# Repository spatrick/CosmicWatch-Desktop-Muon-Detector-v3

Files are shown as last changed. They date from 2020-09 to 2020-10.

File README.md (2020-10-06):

# CosmicWatch-Desktop-Muon-Detector

This repository if for the supplementary material used to build the CosmicWatch Desktop Muon Detectors V3

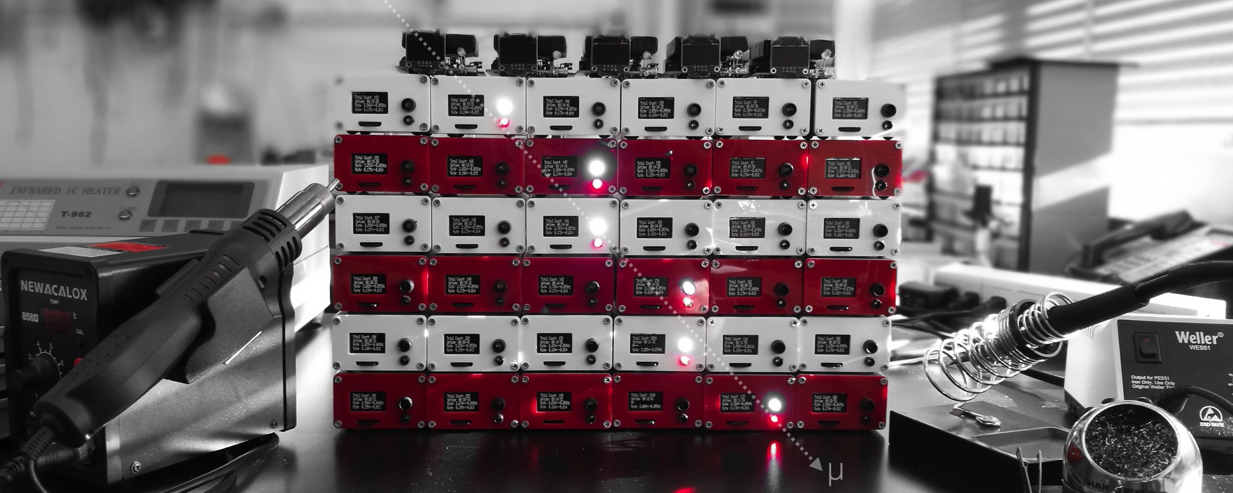
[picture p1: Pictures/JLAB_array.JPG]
screes


Currently, this version of the detector is only used for the MIT Junior Lab. 

Youtube videos describing various aspects of the detectors can be found here:

https://www.youtube.com/watch?v=Js-lOOS7sVE&list=PL4vQqHrEDYfFACdG83gTlRTslMXRjHihq

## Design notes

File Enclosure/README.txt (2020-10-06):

The enclosures were manufactured by enclosures and cases.
http://www.enclosuresandcasesinc.com/

The part number is 2506-2.56” with black and white silk screening on both sides.

The silkscreen, and dimensions are contained in this folder.

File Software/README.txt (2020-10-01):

This folder contains:

1. The Software.ino code. 
This file is the brains of the detector. You can upload it to the detector yourself, if you like, by installing the Arduino IDE, and then TeensyDuino. The code is well annotated, and if you don't plan on adding any extra features, I've added a couple of user options in the first few lines of the code.

2. The pitches.h file is simple the definition of various notes. That's right, you can have your detector play music.	You do not need to know how to use this file.

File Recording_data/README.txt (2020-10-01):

This folder contains:

1. The import_data.py code. 
This file can be run using python to communicate with your detector. The purpose of using this, rather than say the microSD card, is that the timestamp of each event would come from the computer rather than the Teensy, and is therefore more likely to be more accurate. You can also use this code to record multiple detectors to a single file. If you connect multiple detectors to your computer via a USB hub (or multiple USB ports), you can select multiple detectors to record data from using a ',' between names when prompted. This code requires several libraries, including Pyserial and Tornado -- these are available through pip.

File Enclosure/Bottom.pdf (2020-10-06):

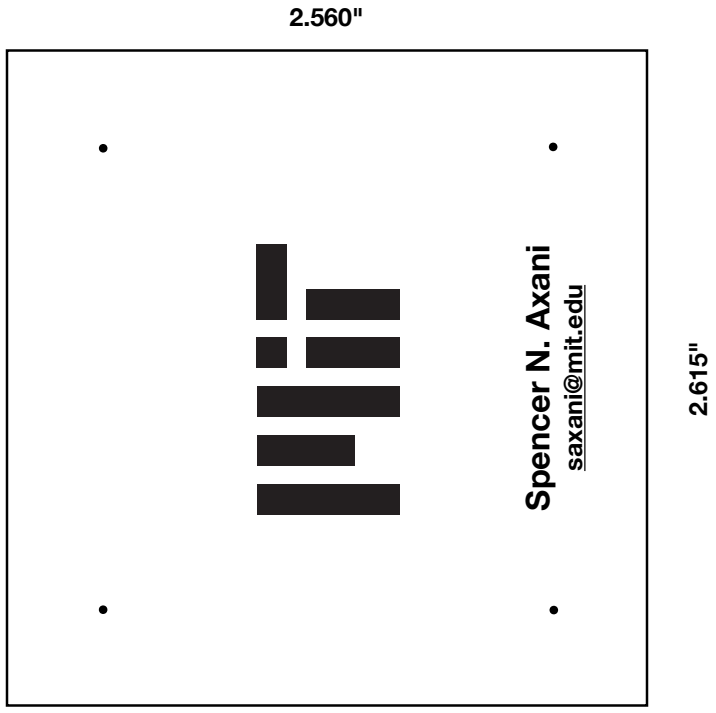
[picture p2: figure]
Spencer N. Axani; saxani@mit.edu

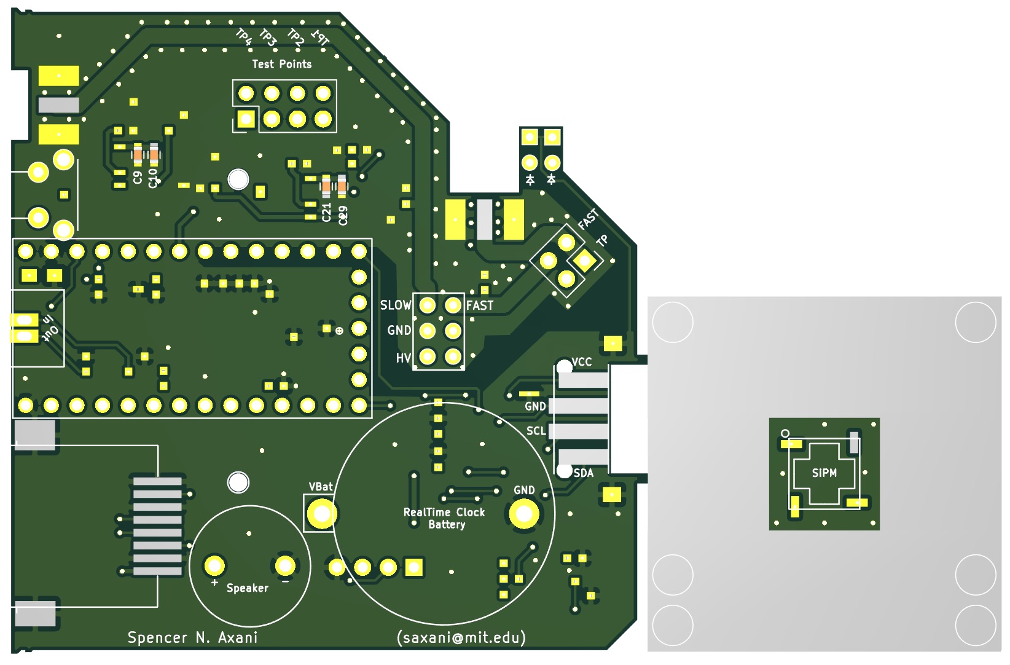
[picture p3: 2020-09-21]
Electronics/PCB_Top.JPG

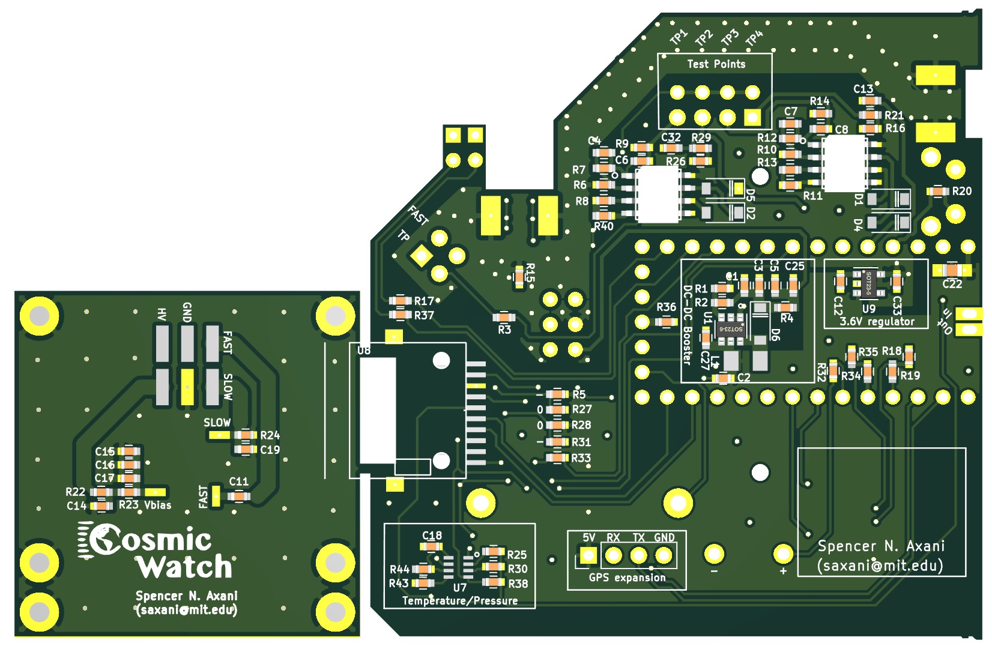
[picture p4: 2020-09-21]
Electronics/PCB_Bottom.JPG

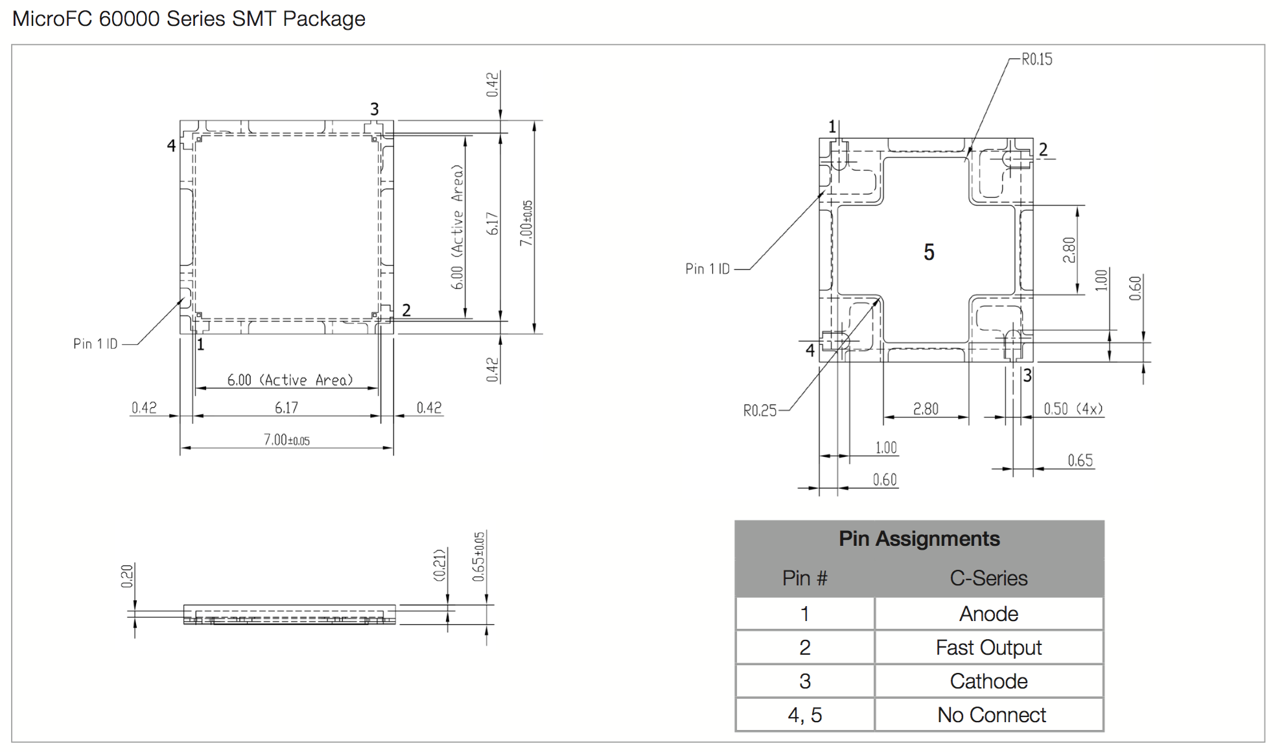
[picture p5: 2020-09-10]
Technical_drawings/SiPM.png

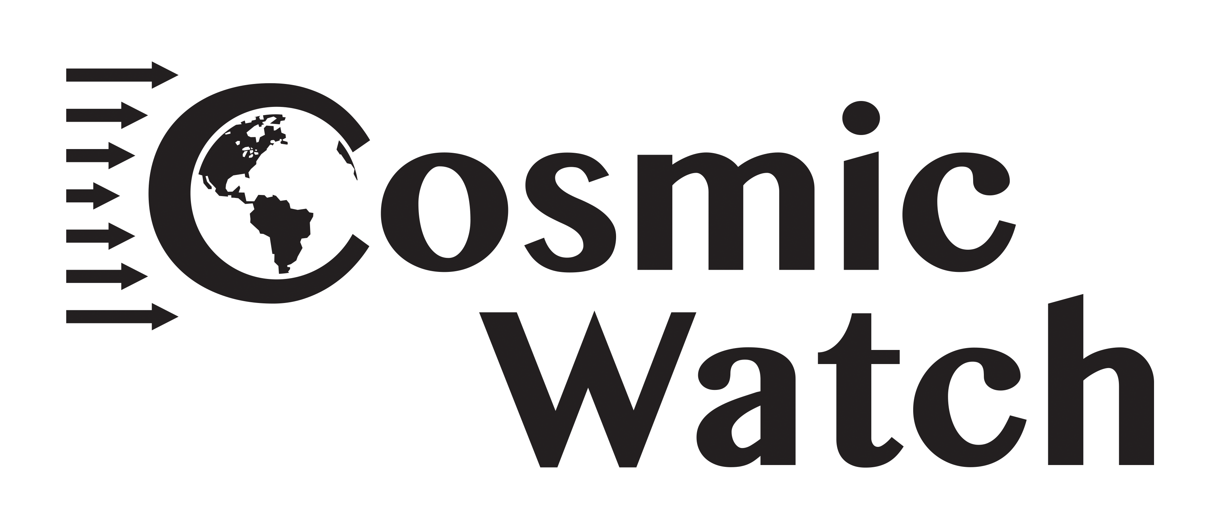
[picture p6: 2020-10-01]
Plotting/Example_data/CosmicWatch_Black.png

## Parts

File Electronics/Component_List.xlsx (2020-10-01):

Component List |  | Buy Extras
Item | Name | Number needed | Unit cost | Discription | Link
1 | SiPM | 1 | 66$ | MICROFC-60035-SMT-TR1 | https://www.digikey.com/product-detail/en/on-semiconductor/MICROFC-60035-SMT-TR1/MICROFC-60035-SMT-TR1OS-ND/9744774
2 | Reset button | 1 | 0.01 | SWITCH TACTILE SPST-NO 0.02A 15V | Digikey part number: P12215S-ND
3 | 3.6V regulator | 1 | 0.01 | TCR2EF36LM(CTCT-ND | https://www.digikey.com/product-detail/en/toshiba-semiconductor-and-storage/TCR2EF36-LM-CT/TCR2EF36LM-CTCT-ND/10380155
4 | DC-DC Booster | 1 | 0.01 | Boost Switching Regulator IC Positive Adjustable 3V 1 Output 260mA (Switch) SOT-23-6 | Digikey part number: MAX5026EUT+TCT-ND
5 | Op Amp LT1807 | 2 | 0.01 | General Purpose Amplifier 2 Circuit Rail-to-Rail 8-SO | Digikey part number: LT1807CS8#PBF-ND
6 | BMP280 temp/pressure | 1 | 0.01 | Pressure Sensor 4.35PSI ~ 15.95PSI (30kPa ~ 110kPa) Absolute 16b 8-SMD | Digikey part number: 828-1064-1-ND
7 | 6-pin connector | 1 | 0.01 | 6-pin connector for SiPM PCB | Digikey Part Number: WM17457-ND
8 | 6-pin header | 1 | 0.01 | 6-pin header for Main PCB | Digikey Part Number: 1212-1229-ND
9 | Jumper | 2 | 0.01 | CONN JUMPER SHORTING .100" GOLD | Digikey Part number: S9337-ND
10 | RJ45 Connector | 1 | 0.01 | CONN MOD JACK 8P8C R/A SHLD | Digikey Part Number: RJLSE4118101-ND
11 | 2.32k resistors | 1 | 0.01 | RMCF0603FT2K32CT-ND | https://www.digikey.com/product-detail/en/stackpole-electronics-inc/RMCF0603FT2K32/RMCF0603FT2K32CT-ND/2418013
12 | 13pF capacaitor | 2 | 0.01 | 1292-1483-1-ND | https://www.digikey.com/product-detail/en/walsin-technology-corporation/0603N130J500CT/1292-1483-1-ND/9355487
13 | 147k resistor | 1 | 0.01 | RES 147K OHM 1% 1/10W 0603 | RMCF0603FT147K‎
14 | 6.65k | 1 | 0.01 | RES 6.65K OHM 1% 1/10W 0603 | RMCF0603FT6K65‎
15 | 0Ohm resistor | 1 | 0.01 | RES 0 OHM JUMPER 1/10W 0603 | RMCF0603ZT0R00‎
16 | 49.9 resistor | 1 | 0.01 | RES 49.9 OHM 1% 1/10W 0603 | RMCF0603FT49R9‎
17 | 10nF capacitor | 1 | 0.01 | CAP CER 10000PF 50V X7R 0603 | 0603B103K500CT‎
18 | 1uF capacitor | 1 | 0.01 | CAP CER 1UF 50V X5R 0603 | ‎CL10A105KB8NNNC‎
19 | 100 resistor | 1 | 0.01 | RES 100 OHM 1% 1/10W 0603 | RMCF0603FT100R‎
20 | 1k resistor | 1 | 0.01 | RES 1K OHM 1% 1/10W 0603 | RMCF0603FT1K00‎
21 | 150 | 2 | 0.01 | RES 150 OHM 1% 1/10W 0603 | RMCF0603FT150R‎
22 | 10k | 1 | 0.01 | RES 10K OHM 1% 1/10W 0603 | RMCF0603FT10K0‎
23 | 6.8uF tantalum cap | 1 | 0.01 | CAP TANT 6.8UF 10% 16V 1206 | 478-1670-1-ND (https://www.digikey.com/product-detail/en/avx-corporation/TAJA685K016RNJ/478-1670-1-ND/564702)
24 | 47uH inductor | 1 | 0.01 | FIXED IND 47UH 170MA 1.3 OHM SMD | Digikey Part Number: 490-4063-1-ND
25 | Schottky diode | 2 | 0.01 | DIODE SCHOTTKY 40V 500MA SOD123 | Digikey Part Number: MBR0540CT-ND
26
27 | Standoff for SiPM PCB | 2 | 0.42 | 1/8" Hex Size, 7/16"" Length, 0-80 Thread Size | McMasterCarr part number: 91780A029
28 | Standoff threaded screws 0-80 | 4 | 1.00 | 0-80 Thread Size, 1/4" Long | McMasterCarr part number: 91771A055
29 | Plastic scintillator screws | 4 | 1.00 | 18-8 Stainless Steel, Number 0 Size, 5/16" Long | McMasterCarr part number: 92470A024
30
31 | microSD cards | 1 | 3$ | 6 packs of 10, 16GB | https://www.amazon.com/gp/product/B07RPVH4QQ/ref=ppx_yo_dt_b_asin_title_o03_s00?ie=UTF8&th=1
32 | 5mm Red LED | 1 | 0.01 | 1 pack of 100
33 | 3mm Red LED | 1 | 0.01 | 1 pack of 100 | https://www.amazon.com/Transparent-Lighting-Electronics-Components-Emitting/dp/B01AUI4VX8
34 | Micro USB cables | 1 | 0.01 | 10inch usb cable | https://www.amazon.com/DETHINTON-Braided-Charging-Samsung-Motorola/dp/B077S58W99
35 | OLED screen | 1 | 0.01 | 10 x 6pcs OLED screens. Need 60 screens. | https://www.amazon.com/Dorhea-Display-SSD1306-Self-Luminous-Raspberry/dp/B07WPCPM5H
36 | SMA connectors | 2 | 0.01 | side mount, with nut , we need a totla of 120 of them. | ` (https://www.amazon.com/Yootop-Female-Connectors-Center-Connector/dp/B07CMNDD3J?cv_ct_cx=sma+connectors)
37 | Test point headers | 1 | 0.01 | 90 degree header. Need 1x 10pcs 40pin | https://www.amazon.com/gp/product/B07XT8DYMW/ref=ox_sc_saved_title_1?smid=A10PG8DP5LW0Q1&psc=1
38 | Buzzer | 1 | 0.01 | Sound buzzer | https://www.amazon.com/Gikfun-Terminals-Passive-Electronic-Arduino/dp/B01GJLE5BS
39 | Battery case | 1 | 0.01 | 50 total batteries is fine | https://www.amazon.com/gp/product/B01JYNDZF0/ref=ppx_yo_dt_b_asin_title_o03_s00?ie=UTF8&psc=1
40 | Battery | 1 | 0.01 | 50 total batteries is fine | https://www.amazon.com/gp/product/B078GC5K81/ref=ppx_yo_dt_b_asin_title_o03_s00?ie=UTF8&psc=1
41 | RJ45 cable | 1 | 0.01 | we need 60 RJ45 cables, 6inch is what I'm suggesting | https://www.amazon.com/gp/product/B07ZNWSVLV/ref=ppx_yo_dt_b_asin_title_o06_s01?ie=UTF8&psc=1
42 | Header pins for Teensy | 1 | 0.01 | 1 pack of headers is fine | https://www.amazon.com/Breakaway-Header-Straight-Connector-Prototype/dp/B07BXDYTBP
43 | Electrical tape | 1 | 0.01 | 6pack of tape should work | https://www.amazon.com/Cambridge-Electrical-Black-Professional-Listed/dp/B0143LD8QY
44 | Aluminum foil | 1 | 0.10 | 100cm^2 aluminum foil | https://www.amazon.com/Amazon-Brand-Solimo-Aluminum-Square/dp/B07WDNGB82
45
46 | PCB | 1 | 1.00 | Printed circuit board | https://www.elecrow.com/pcb-manufacturing.html
47 | Acrylic faceplates | 1 | 1.00 | Front and back face plates | https://www.elecrow.com/acrylic-cutting.html
48 | Aluminum case | 1 | 5.00 | 2506-2.56" Clear Anodize case with 8 screws | http://www.enclosuresandcasesinc.com/
49
50 | Teensy4.0 | 1 | 20$ |  | https://www.pjrc.com/store/teensy40.html

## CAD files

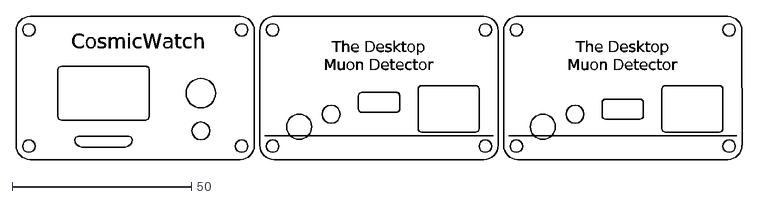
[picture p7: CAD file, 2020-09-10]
Technical_drawings/Faceplates.dxf
CosmicWatch
The Desktop Muon Detector

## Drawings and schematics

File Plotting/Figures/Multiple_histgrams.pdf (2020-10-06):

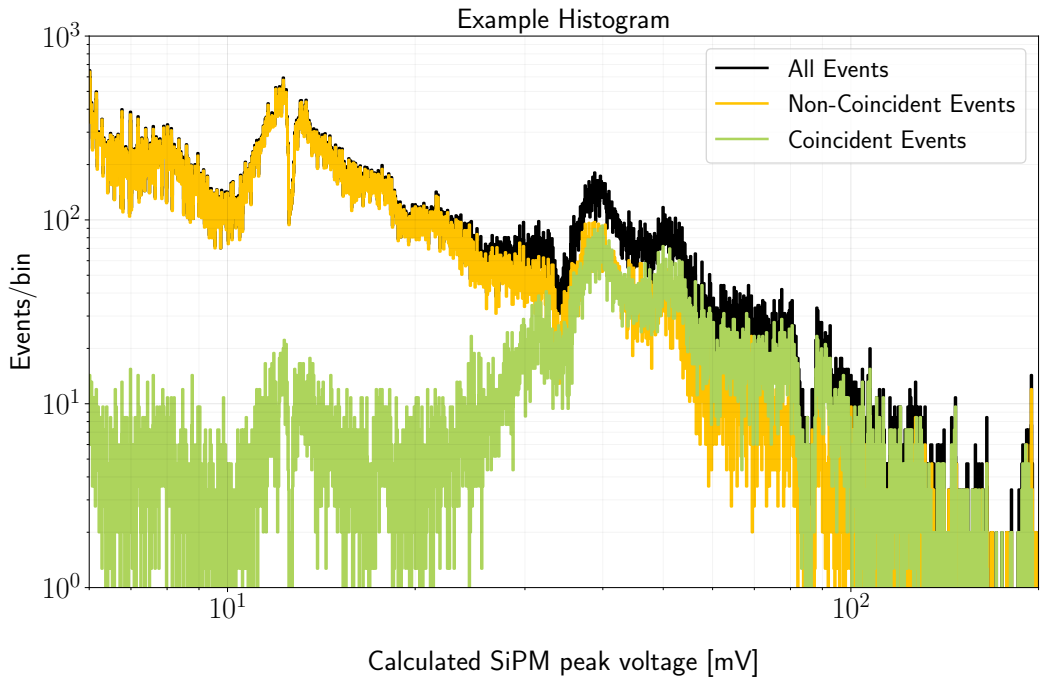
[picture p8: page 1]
Events/bin; Example Histogram; All; Events

Non-Coincident Events
Coincident Events

Calculated SiPM peak voltage [mV]

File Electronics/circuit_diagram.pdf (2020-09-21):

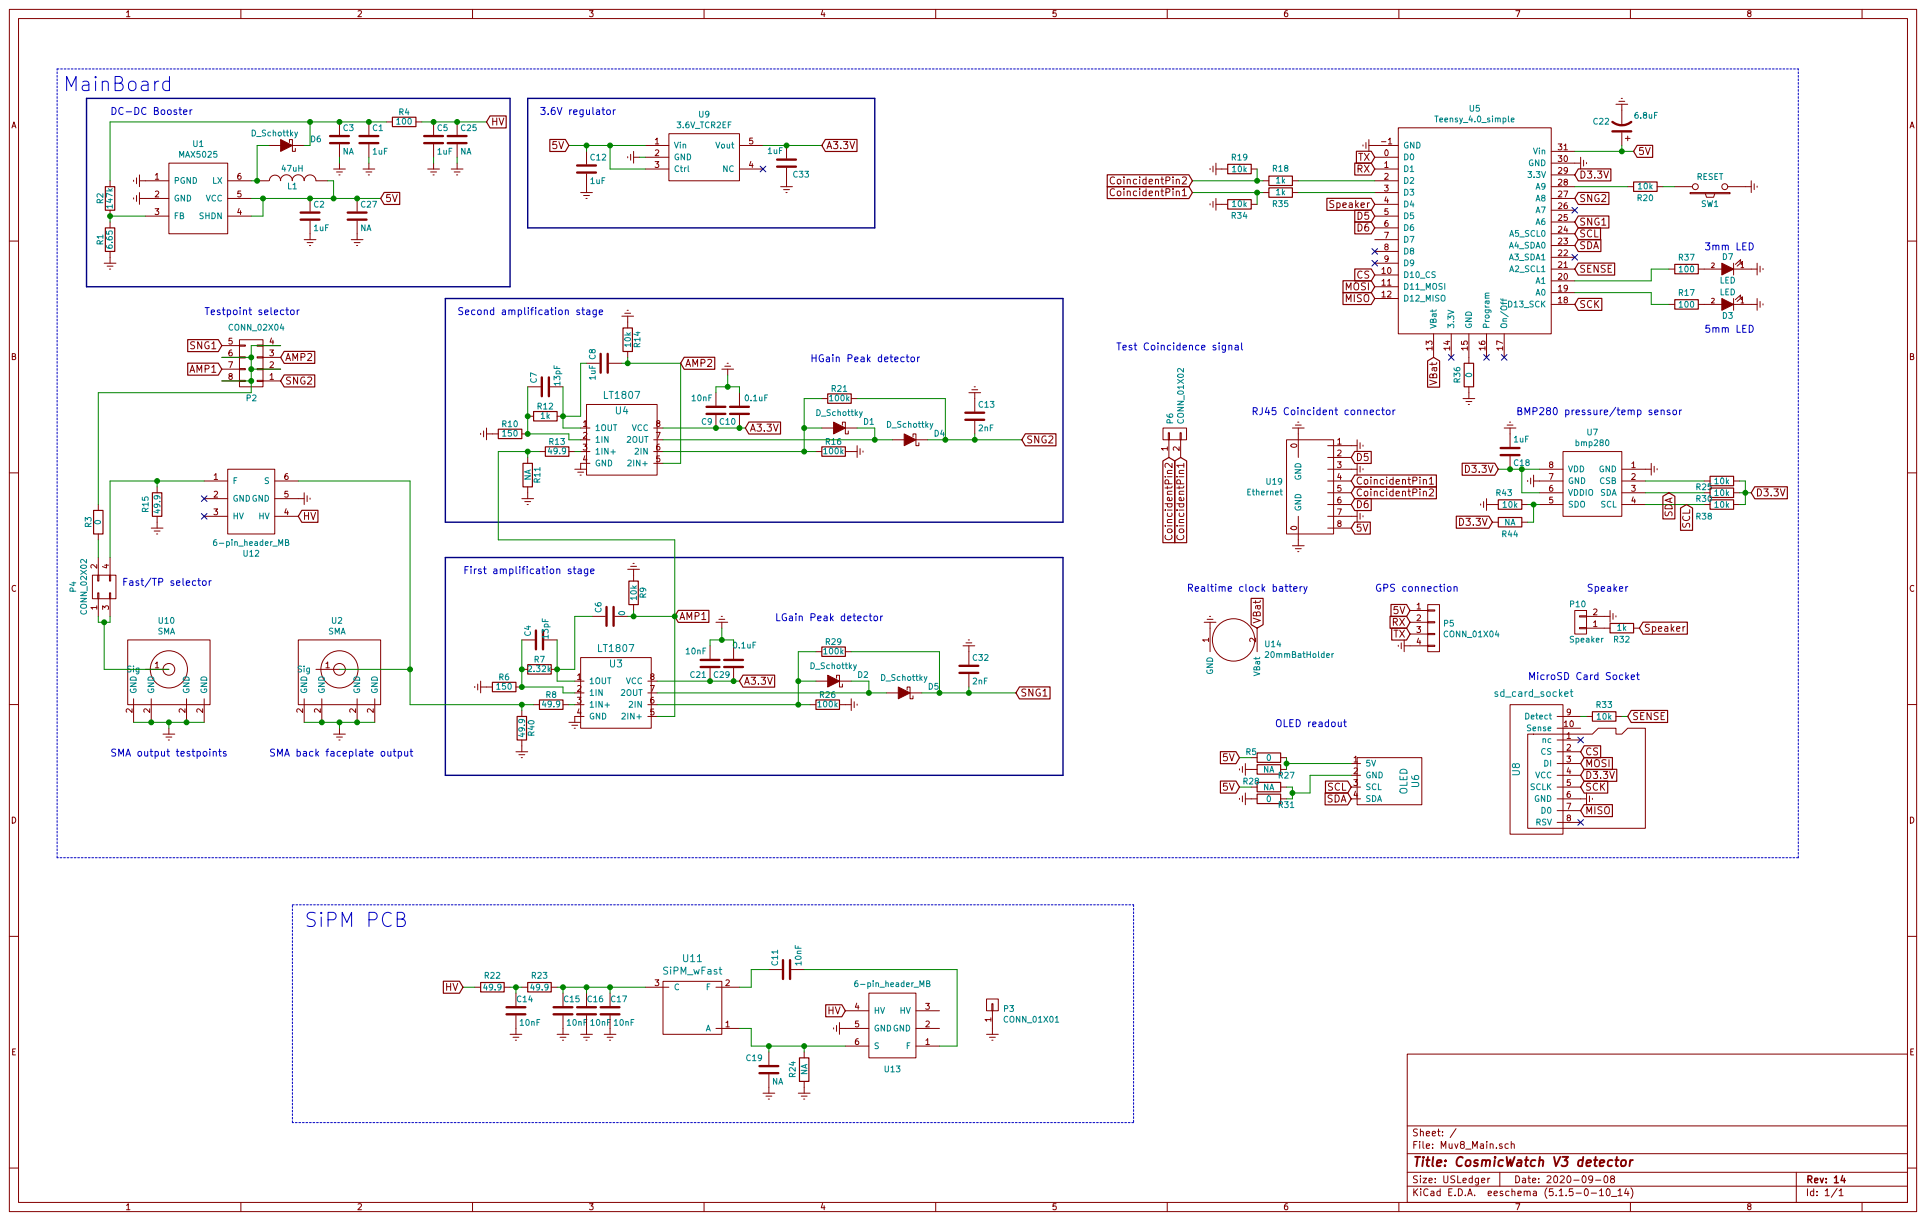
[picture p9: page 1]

Id: 1/1 Title: CosmicWatch V3 detector

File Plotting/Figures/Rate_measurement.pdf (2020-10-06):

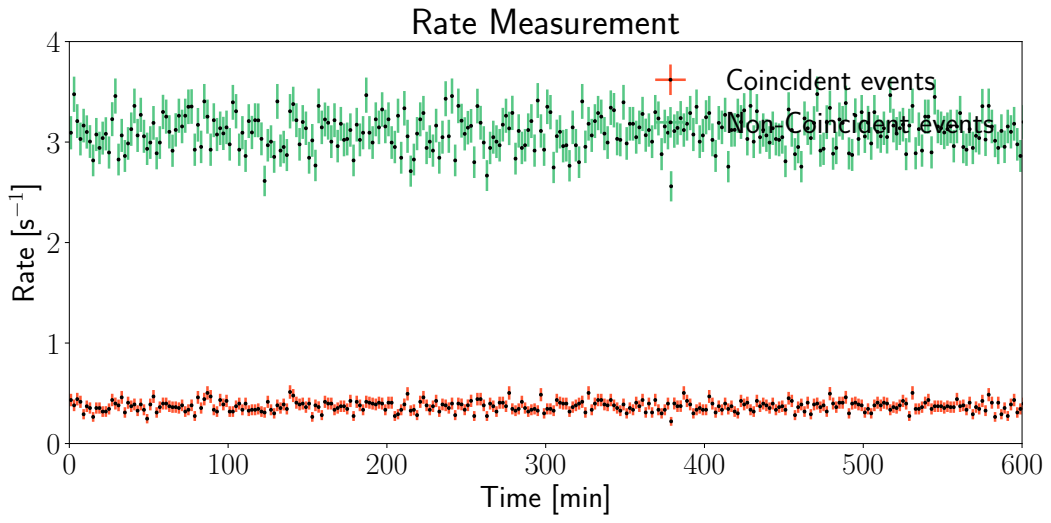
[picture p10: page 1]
Time [min]; Rate [s; Rate Measurement; Coincident events; Non-Coincident; events

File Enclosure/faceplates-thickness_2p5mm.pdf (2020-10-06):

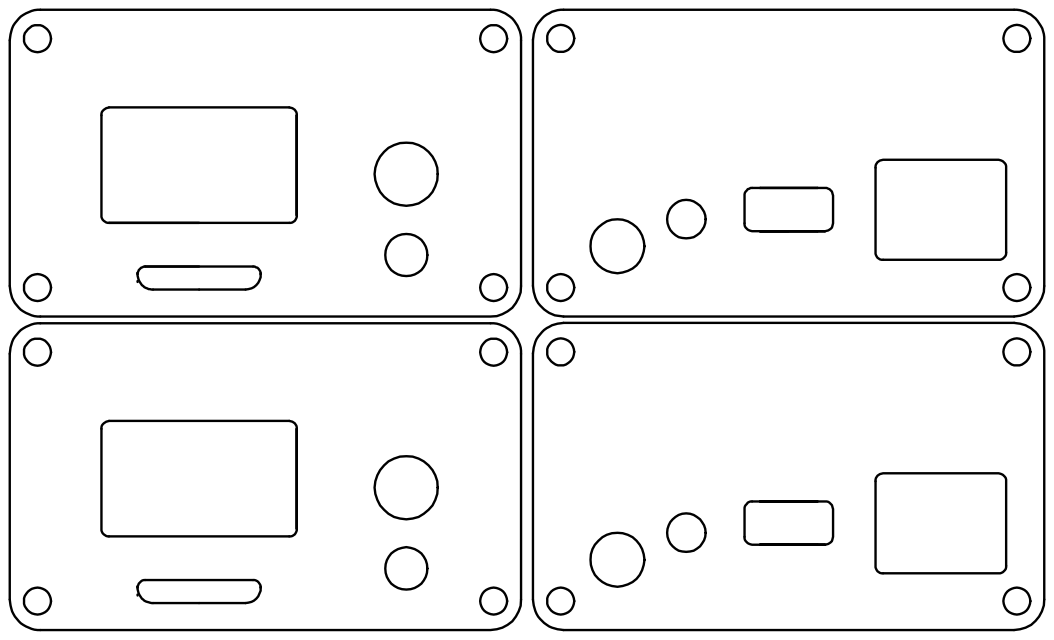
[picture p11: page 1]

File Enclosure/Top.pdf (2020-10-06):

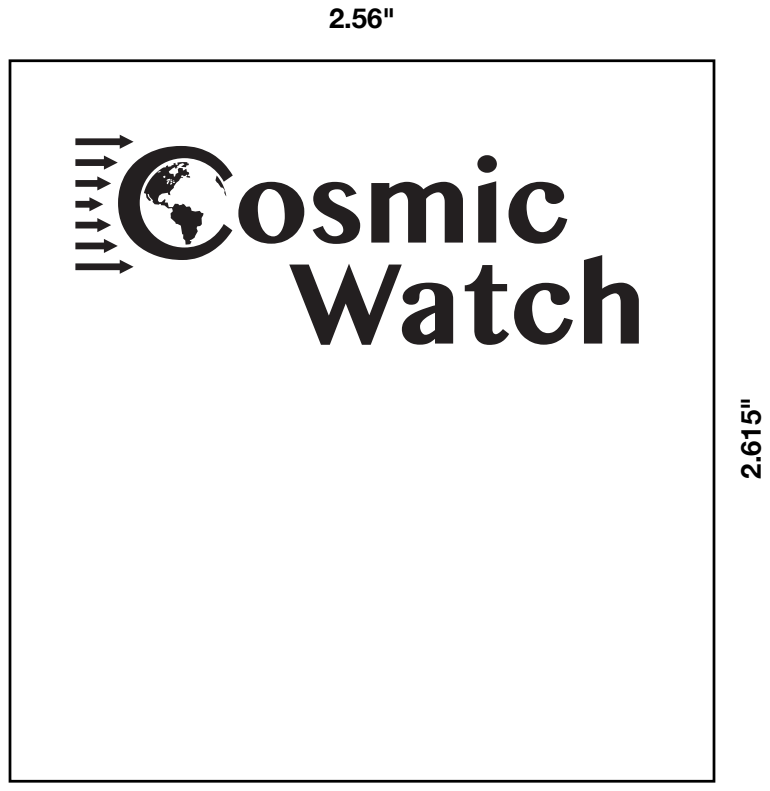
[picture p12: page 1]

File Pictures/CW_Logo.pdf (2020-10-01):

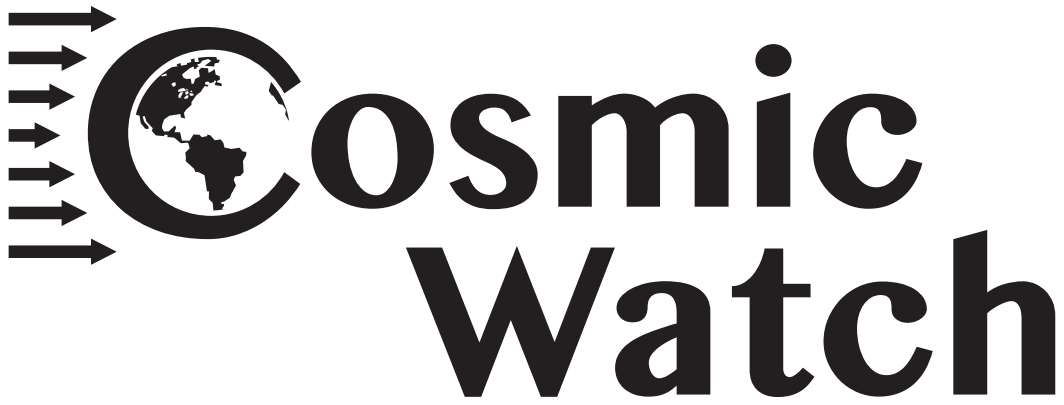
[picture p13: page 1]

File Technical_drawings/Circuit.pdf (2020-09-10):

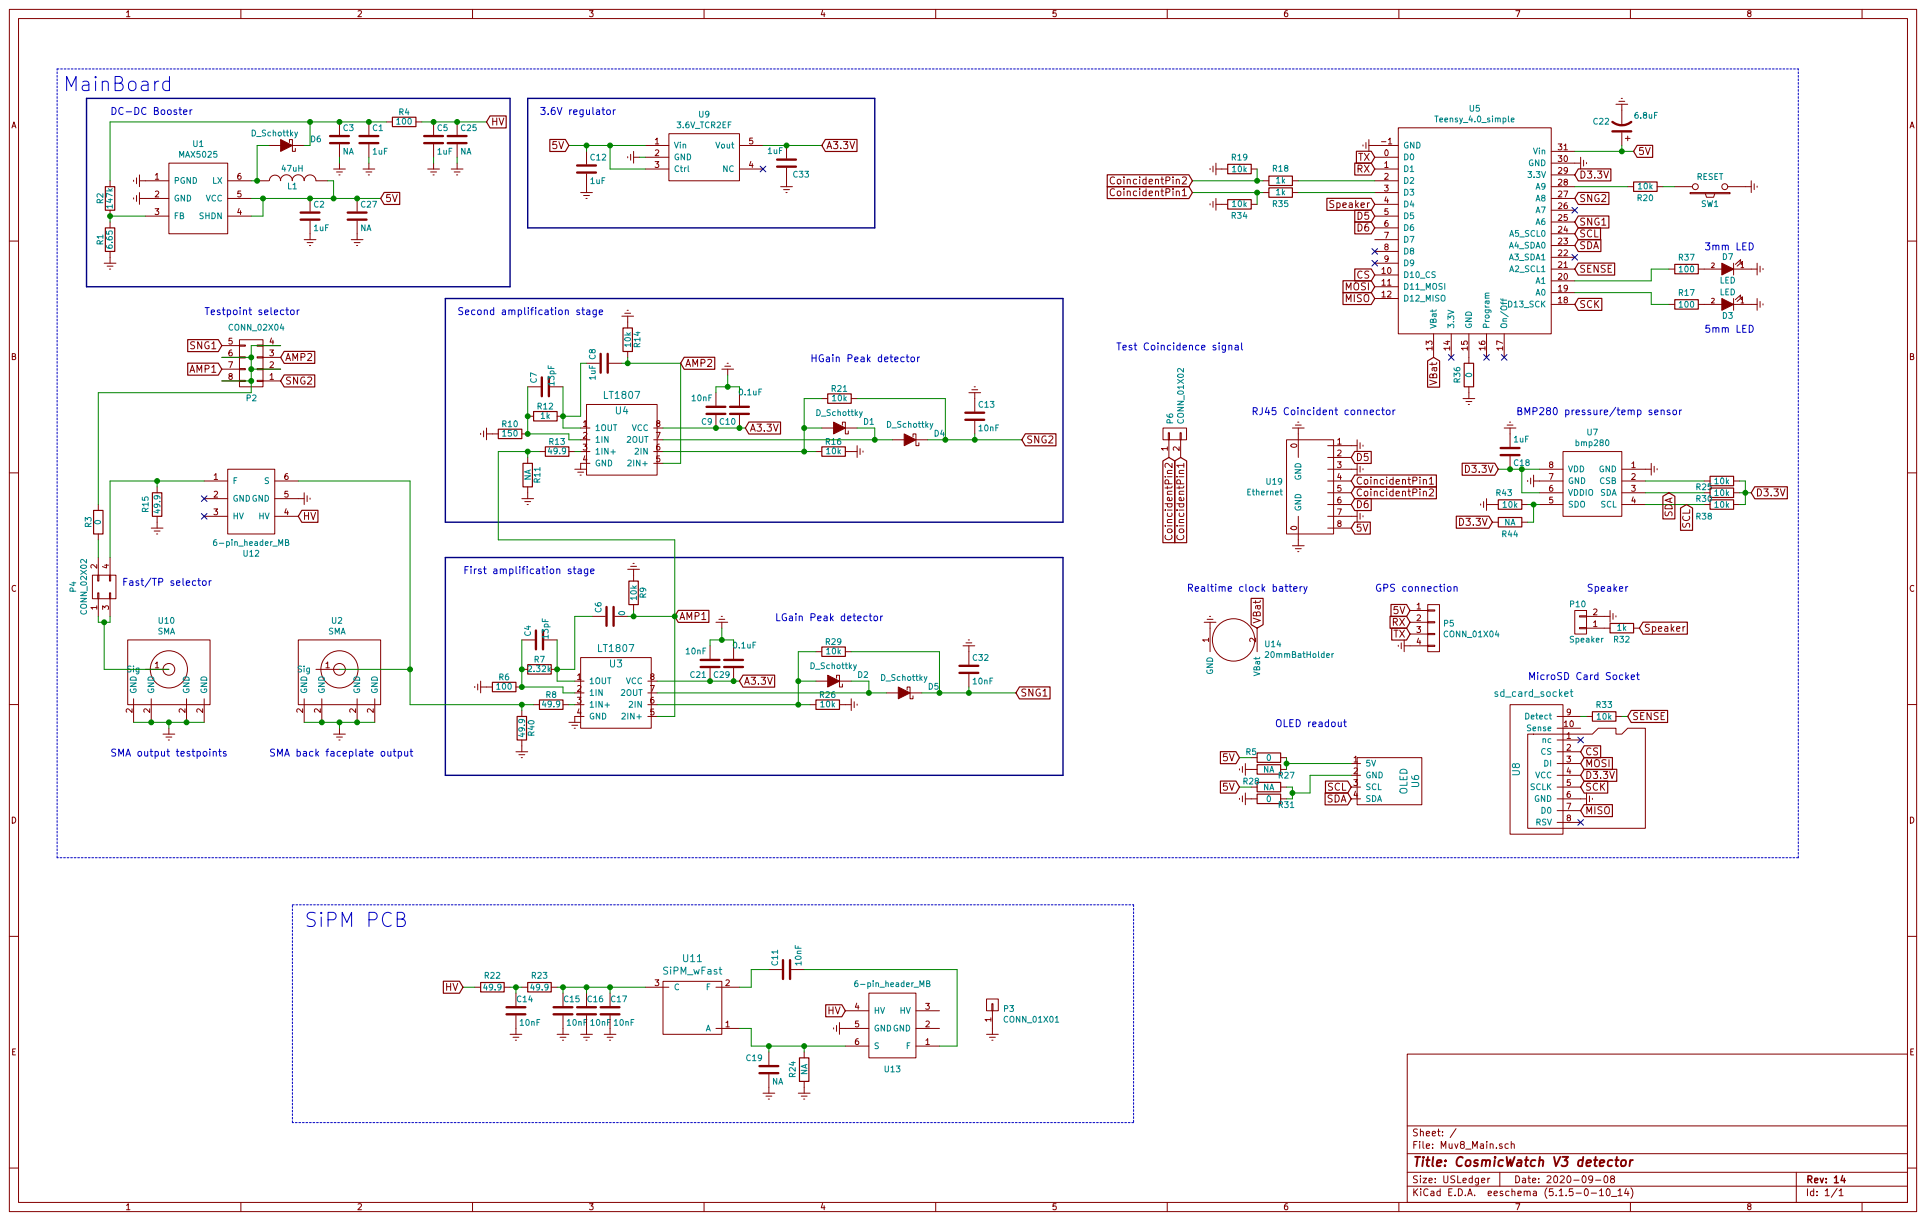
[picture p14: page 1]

Id: 1/1 Title: CosmicWatch V3 detector

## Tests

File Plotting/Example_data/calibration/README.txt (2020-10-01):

This folder contains:

1. The cal.txt. 
This file contains the detector calibration. It is used to convert from measured ADC values to SiPM peak voltages.

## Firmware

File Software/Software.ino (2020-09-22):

// Tools-> Board = Teensy 4.0
// Tools-> Port = Select the port corresponding to where the detector is plugged in.
// Libraries needed. Go to Sketch->Include Libraries-> Manage Libraries and install:
//   1. Adafruit_SSD1306
//   2. Adafruit_BMP280
//   3. SDFat

const boolean RESET_DETECTOR_NAME = false;        // Do you want to update the name of the detector?
String desired_detector_name      = "Five";     // If so, then to what?

int SHIFT_HOUR                    = 0;           // The realtime clock  doesn't understand daylight savings, sometimes you have to shift the hour.

int SIGNAL_THRESHOLD              = 50;          // The number of HGain ADC counts above the baseline before triggering
int RESET_THRESHOLD               = 25;           // Number of ADC counts above the baseline before resetting the trigger
const boolean OLED                = true;         // Turn on/off OLED. 
const int LED_BRIGHTNESS          = 255;          // Brightness of the 5mm LED [0,255]
const int LED_BRIGHTNESS_SMALL    = 255;          // Brightness of the 3mm LED [0,255]
const boolean SAVE_ALL_EVENTS     = true;        // Do you want to save all events? Set to false if you only want to save muons.

// Set these to false to turn off noise.
const boolean PLAYSTARTMUSIC      = false;         // Play music during startup
const boolean PLAYEVENTNOISE      = false;         // Make a noise during an event.

// You don't need this.
const boolean CALIBRATE           = false;        // Do you want to calibrate the detector? 
const boolean VERBOSE             = true;         // print out detector information through the serial port.

//############################################################################################################################



// A boolean to store whether or not another detector is plugged in.
boolean COINCIDENCE = false; // Is there another detector plugged into the RJ45 connector?

// Setup the real-time clock
#include <TimeLib.h>

// Setup the reset button.
#define RESTART_ADDR 0xE000ED0C
#define READ_RESTART() (*(volatile uint32_t *)RESTART_ADDR)
#define WRITE_RESTART(val) ((*(volatile uint32_t *)RESTART_ADDR) = (val))
const int reset_pin = 23;

// Setup ADC for measuring the SiPM Pulses
#include <ADC.h>
#include <ADC_util.h>
ADC *adc = new ADC();
float sampling_period = 0; // sampling_period defines how many us it takes to make 1 ADC sample.

// Setup the OLED screen. It would be good to use a different library. This is the dominant source of deadtime.
#include <Adafruit_SSD1306.h>
#define OLED_RESET -1
IntervalTimer myTimer;
Adafruit_SSD1306 display(OLED_RESET);
boolean trigger_OLED_readout = true;

// Setup the temperature/pressure sensor, BMP280
#include <Adafruit_BMP280.h>
#include <Wire.h>
#include <SPI.h>
#define BMP_SCK  (13)
#define BMP_MISO (12)
#define BMP_MOSI (11)
#define BMP_CS   (10)
Adafruit_BMP280 temp_pressure_sensor; // I2C
float event_temperature = 0;          // C
float event_pressure    = 0;          // Pa

      
// Setup the microSD Card writer. The SensePin tells you if a physical SD card is ins
#include "SdFat.h"
SdFat SD;
SdFile myFile;
const uint8_t chipSelect = SS;
char filename[] = "File_000.txt"; // The default file name on the SDCard.
boolean trigger_microSD_readout = true;
IntervalTimer myTimer_microSD;
const int SD_sense_pin = 4;
boolean SDAvailable = true;

// Setup the speaker/buzzer to play sounds.
#include "pitches.h"
const int speaker_pin = 7;
int Event_noteDuration = 8;
int Event_noteKey = _C4;


// Setup the LED pin to flash when there is an event.
const int led_pin  = 14; // LED for all events
const int led_pin_small = 15; // LED for muon-only events.

// Setup the code for the detector name.
#include <EEPROM.h>
const int EEPROM_MIN_ADDR = 0;
const int EEPROM_MAX_ADDR = 511;
const int BUFSIZE = 40;
char detector_name[BUFSIZE]; // The detector name 
int chars_in_detector_name = 0;

// Event buffer information. Each entry in the array will correspond to an event.
float         event_SiPM_peak_voltage = 0;
byte          event_coincident = 0;
unsigned long int event_timestamp = 0;
float         event_measured_ADC_HGAIN = 0;
float         event_measured_ADC_LGAIN = 0;
unsigned int  event_deadtime = 0;
unsigned int  total_deadtime = 0;
unsigned long int event_number = 0;
unsigned long int coincidence_event_number = 0L;   // A tally of the number of coincidence triggers counts observed
unsigned int event_hour;
unsigned int event_minute;
unsigned int event_second;
unsigned long int event_millis;
unsigned int event_year;
unsigned int event_month;
unsigned int event_day;




// Setup the array to store the ADC values. These are the samples that determine the pulse amplitude.
const int number_of_ADC_samples = 3; 
int adc_values_LGain[number_of_ADC_samples] = {};
int adc_values_HGain[number_of_ADC_samples] = {};

// Initiate the event counter. 
//unsigned long int counter = 0L;               // A tally of the number of triggers counts observed
//unsigned long int coincidence_counter = 0L;   // A tally of the number of coincidence triggers counts observed

// Setup the RJ45 communication. This sends digital pulses to other detectors connected with the ethernet cable.
const int coincident_pin_1 = 2;
const int coincident_pin_2 = 3;
int coincident_signal_input_pin = coincident_pin_2;
int coincident_signal_output_pin = coincident_pin_1;

//boolean readout_data = 0;  // Readout data when 1.

unsigned long long start_time                    = 0L;      // Detector start time reference variable


// The following are used to convert a measured ADC value to a SiPM pulse amplitude.
// The numbers here represent the coeffiecients to a polynomial.
const long double calibration_LGAIN[] = {7.770331963379388, 0.8551744828904521, -0.022610435459974862, 
        0.0003373183522713416, -2.7337802203549252e-06, 1.3226510403668739e-08, -4.0439095029897887e-11, 
        8.051241933191732e-14, -1.0542207510231822e-16, 9.042246953474205e-20, -5.069161049407975e-23, 
        1.9481994863843597e-26, -5.8210764000045555e-30, 1.1493759151290367e-33};
const long double calibration_HGAIN[] = {8.50709099942261, -0.11778994093618891, 0.0017674792660310806,
            -1.0974310076889382e-05, 3.860681705887885e-08, -8.15063422576611e-11, 1.0149341982138817e-13,
            -6.819510515623369e-17, 1.8973203130950888e-20};
float turn_over_value = 15.;
float sigmoid_width = 1.5; 
    
// The slopes of the above calibration polynomial fits are used to determine 
// which channel is a better measure of the SiPM pulse amplitude.
long double calibration_HGAIN_slope[sizeof(calibration_HGAIN)/sizeof(long double)]; 
long double calibration_LGAIN_slope[sizeof(calibration_HGAIN)/sizeof(long double)];

// Setup external calibration. This is to determine how to convert from ADC to SiPM peak voltage
unsigned int  n_samples = 200;         // How many samples to take per voltage level
int           step_size_low = 1;       // Detector start time reference variable
int           start_value_low = 5;     // Detector start time reference variable
int           step_size_mid = 2;      // Detector start time reference variable
int           start_value_mid = 20;    // Detector start time reference variable
int           step_size_high = 10;     // Detector start time reference variable
int           start_value_high = 50;    // Detector start time reference variable
int           desired_input_voltage = start_value_low;
int           delay_between_measurements = 5000;

//baseline properties
int n_baseline_samples = 100.;
int HGain_baseline = 0;
int LGain_baseline = 0;
float baseline_average = 0;
float baseline_std = 0;

//############################################################################################################################
void setup() {
  // Set the reset button to softRestart the detector.   
  pinMode(reset_pin, INPUT_PULLUP);
  attachInterrupt(digitalPinToInterrupt(reset_pin), soft_restart, FALLING);

  // Start the USB serial communication 
  Serial.begin(115200);

  // Setup the LED to output a flash when an event triggers.
  pinMode(led_pin, OUTPUT);
  pinMode(led_pin_small, OUTPUT);
  
  
  // if RESET_DETECTOR_NAME, this will rename the detector. You have to then change RESET_DETECTOR_NAME to false.
  if (RESET_DETECTOR_NAME){
    set_detector_name();
    if (VERBOSE){
      Serial.println("# Setting device ID: "+(String)desired_detector_name); 
      }
    }
  get_detector_name(detector_name);

  for (int i = 0; i<BUFSIZE; i++){
    if (detector_name[i]){
        chars_in_detector_name += 1;
        }
      }
      
  display.begin(SSD1306_SWITCHCAPVCC, 0x3C);
  display.setRotation(2);         // Upside down screen (0 is right-side-up)
  OpeningScreen();                // Run the splash screen on start-up
  check_for_coincident_detector(); 

  

  // The SD sense pin checks to see if an SD card is inserted.
  pinMode(SD_sense_pin, INPUT_PULLUP);

  // Start the temp and pressure sensor
  temp_pressure_sensor.begin(0x76);
  temp_pressure_sensor.setSampling(Adafruit_BMP280::MODE_NORMAL,     /* Operating Mode. */
                  Adafruit_BMP280::SAMPLING_X2,     /* Temp. oversampling */
                  Adafruit_BMP280::SAMPLING_X16,    /* Pressure oversampling */
                  Adafruit_BMP280::FILTER_X16,      /* Filtering. */
                  Adafruit_BMP280::STANDBY_MS_500); /* Standby time. */
  

  // Get the detector name from the EEPROM
  if (VERBOSE){
    if (chars_in_detector_name > 20){
      Serial.println("# Det Name too large. Keep <= 20 characters.");
    }
    Serial.println("# Found detector ID: "+(String)detector_name); 
  }
    // Start up the OLED screen
  
  if (VERBOSE){
    look_for_devices();
    Serial.println("# The default address for OLED: 0x3C"); 
    Serial.println("# The default address for BMP280 temperature/pressure sensor: 0x76");
  }

  if (!SD.begin(chipSelect, SD_SCK_MHZ(50))) {
    Serial.println(F("# SD initialization failed!"));
    Serial.println(F("# Is there an SD card inserted?"));
    //SD.initErrorHalt();
    SDAvailable = false;
  }
  
  /*
  if (!SD.begin()) {
    Serial.println(F("# SD initialization failed!"));
    Serial.println(F("# Is there an SD card inserted?"));
  }
  */
  setup_sd_card_files();
  OpeningInfo();
  
  if (digitalRead(SD_sense_pin) == LOW) {
    if (VERBOSE){
    Serial.println("# MicroSD card inserted.");
    }
  }
  
  if (digitalRead(SD_sense_pin)==HIGH) {
    if (VERBOSE){
    Serial.println("# No MicroSD card inserted.");
    }
  }
  
  if (Serial){
    if (VERBOSE){
    Serial.println("# I see serial communication.");
    }
   }

  // Setup the ADC to make some high-frequency measurements.
  adc->adc0->setAveraging(1);
  adc->adc0->setResolution(10);
  adc->adc0->setSamplingSpeed(ADC_SAMPLING_SPEED::VERY_HIGH_SPEED);
  adc->adc0->setConversionSpeed(ADC_CONVERSION_SPEED::VERY_HIGH_SPEED);

  // Measure the baseline mode, average, and std. Also measure the sample rate of the ADC.
  measure_baseline();

  
  // This gets the time from the computer to set the real-time clock
  
  setSyncProvider(getTeensy3Time);
  if (Serial){
    
    if (VERBOSE){
      if (timeStatus()!= timeSet) {
        Serial.println("# Unable to sync with the RTC");
      } else {
        Serial.println("# RTC has set the system time");
      }
    }
  }
  
  if (CALIBRATE){
    Serial.println("# Calibration is active. ");
    }

  display.clearDisplay();  
  delay(1500);                    // Delay some time to show the logo, and keep the Pin6 HIGH for coincidence




  // Calculate the slopes of the calibration curves. 
  //calculate_calibration_slopes();
  

  // Update the OLED every second
  myTimer.begin(trigger_OLED, 1000000);
  //myTimer.priority(255);

  // write to the sd card every 10seconds
  myTimer_microSD.begin(trigger_microSD, 10000001);


  // Print the header information to the file.
  print_header();
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

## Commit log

2020-10-01 Improving Documentation
    [Component_List.xlsx]
2020-10-06 Cleaning up repo
    [faceplates.dxf]
